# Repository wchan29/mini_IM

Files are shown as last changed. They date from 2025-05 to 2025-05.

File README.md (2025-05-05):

# mini_IM 
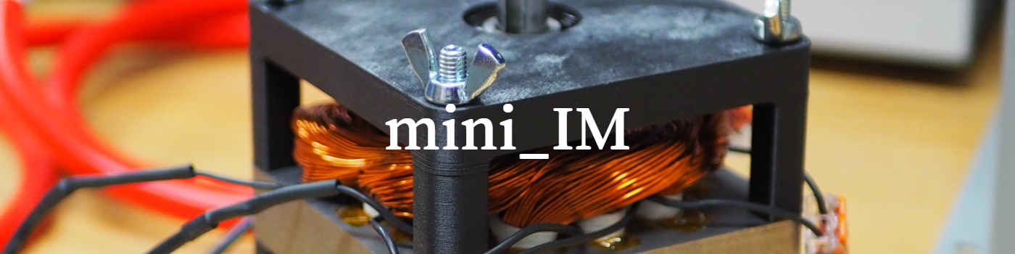
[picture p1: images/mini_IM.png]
mini_IM_banner


[][cc-by-nc]




## About
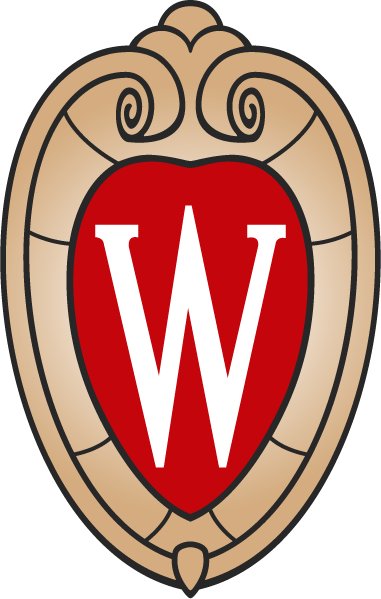
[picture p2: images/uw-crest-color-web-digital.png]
> 
> Compact Induction Machine with 3D Printed Housing. 
> 2021 UW-Madison Senior Design Project.

This project involves the design and prototyping of a compact, low-voltage induction machine kit for future use in UW-Madison's electrical engineering courses. Commissioned by the Grainger Teaching Studio, the kit supports a new hands-on power conversion class. This repository documents iterations developed by the senior design team.

**Team Memeber:** Anson Chan , Jon Keller, Steven Gerbers, Nathan Seibold <br>
**Post**: [Blog Post](https://wchan29.github.io/portfolio/wempec_induction_3d/)

### Rendering
<div style="display: flex; gap: 10px; align-items: flex-start;">
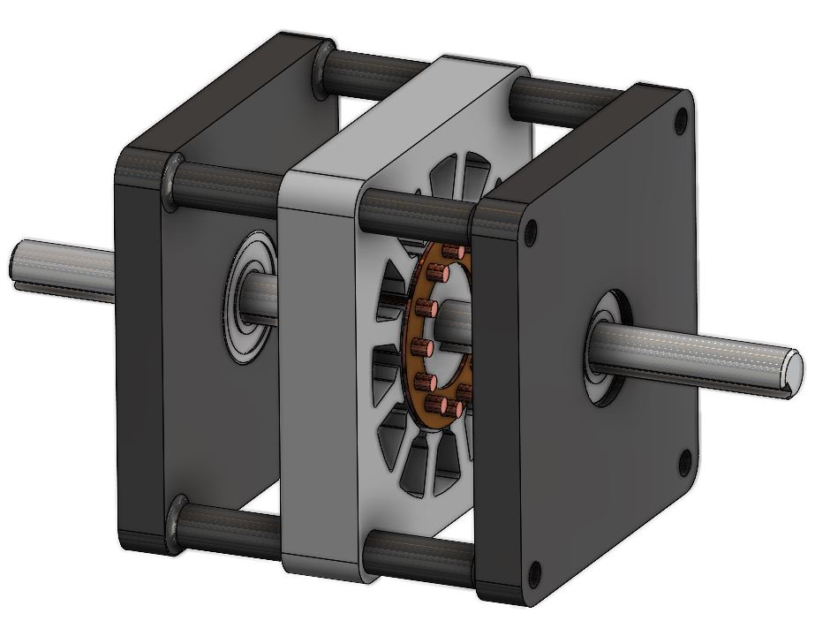
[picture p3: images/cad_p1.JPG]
  
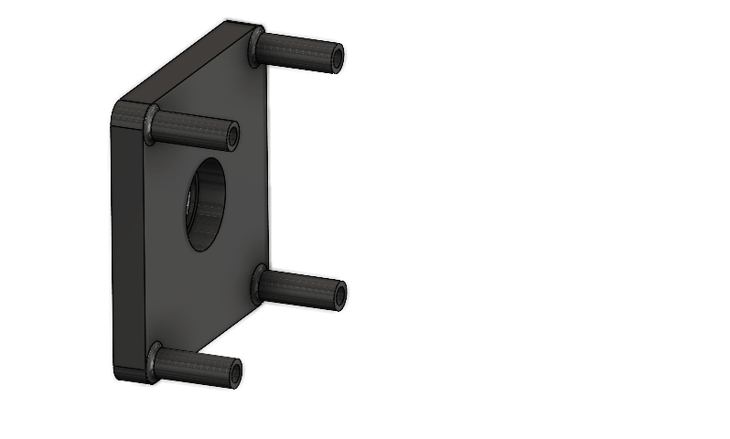
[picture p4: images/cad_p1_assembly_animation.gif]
  
</div>

## License
[][cc-by-nc]

This work is licensed under a
[Creative Commons Attribution-NonCommercial 4.0 International License][cc-by-nc].

[][cc-by-nc]

[cc-by-nc]: https://creativecommons.org/licenses/by-nc/4.0/
[cc-by-nc-image]: https://licensebuttons.net/l/by-nc/4.0/88x31.png
[cc-by-nc-shield]: https://img.shields.io/badge/License-CC%20BY--NC%204.0-lightgrey.svg

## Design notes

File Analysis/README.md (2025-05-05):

# Analysis 
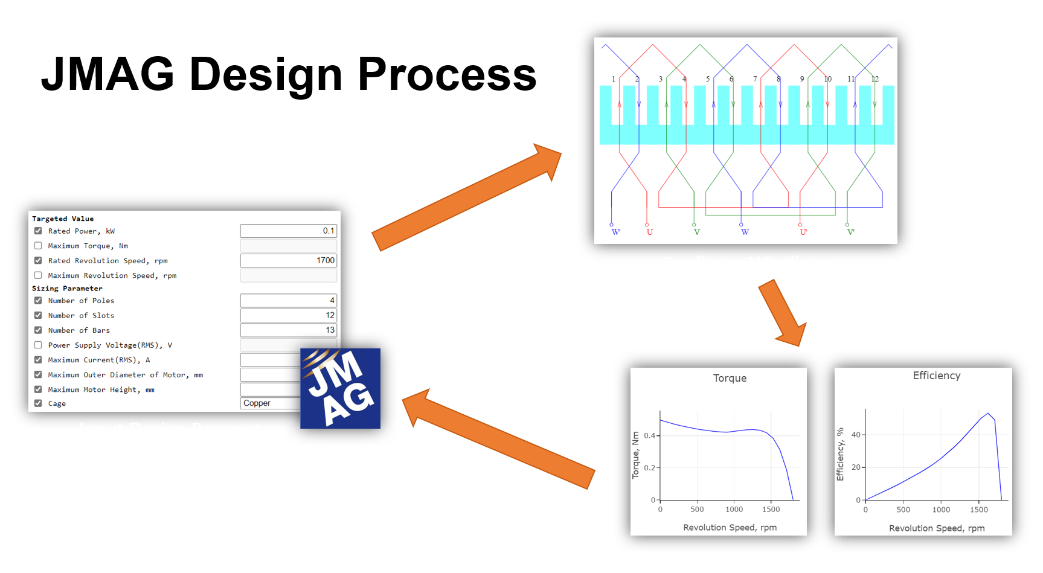
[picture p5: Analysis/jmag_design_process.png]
mag_design_process


## Related Documents
- [pd.jmd](./p3.jmd) - JMAG Express project file for p3 prototype

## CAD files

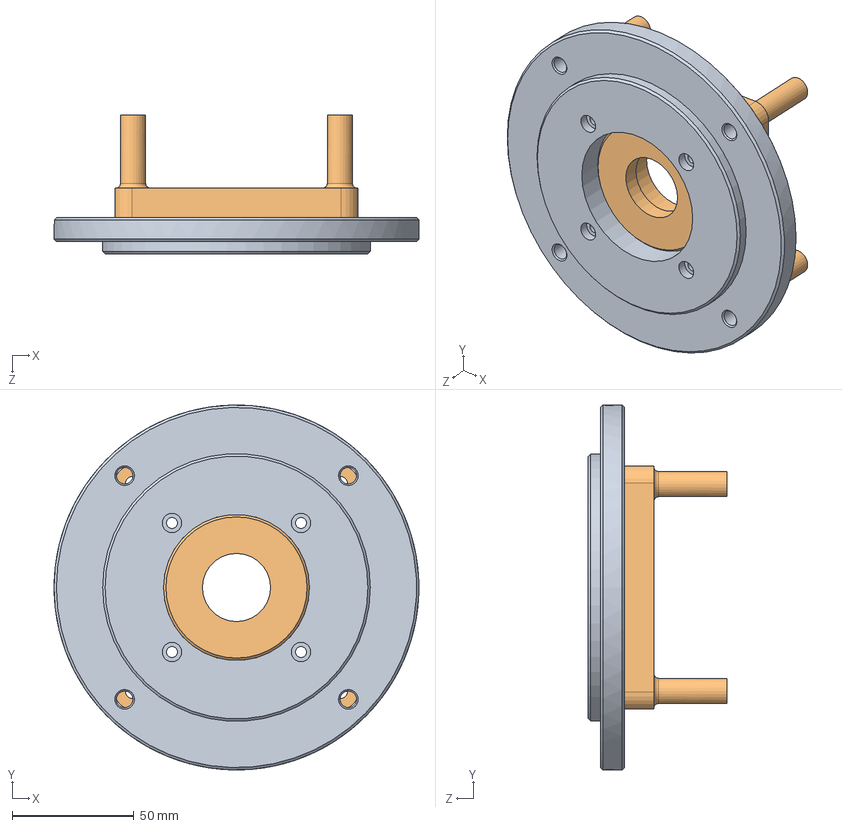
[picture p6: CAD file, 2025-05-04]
CAD/adapter_plate/Assem1.SLDASM
150.0 x 149.9 x 57.0 mm
adapter_plate
housing_plate

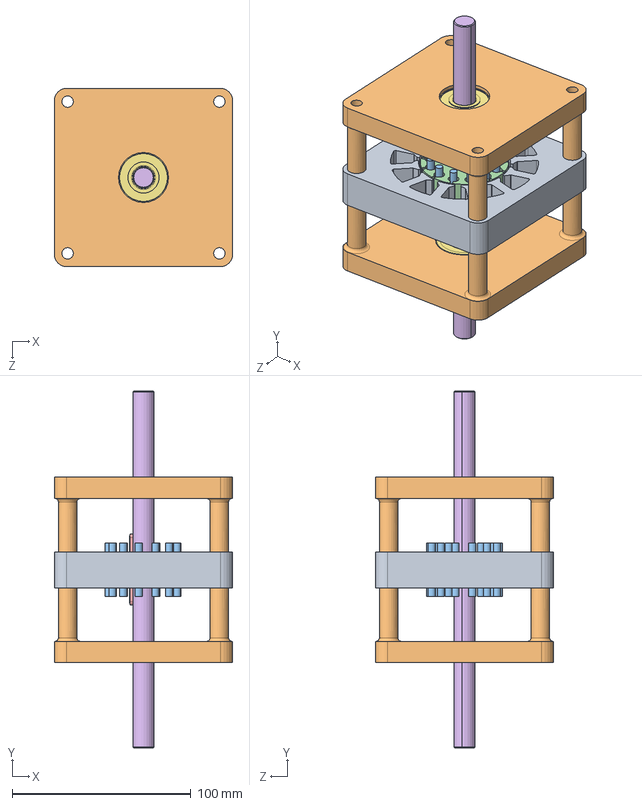
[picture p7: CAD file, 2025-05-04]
CAD/prototype_2/!p2_PrototypeAssmebly.SLDASM
100.0 x 200.0 x 100.0 mm
p2_stator_lamination
p2_housing_plate x 2
p2_copper_bars x 13
p2_rotor_lamenation
p2_shaft_key_KES4_40
p2_shaft_SFHKR12_200_KA80_A40
p2_Ball_Bearing_B6201ZZNR x 2

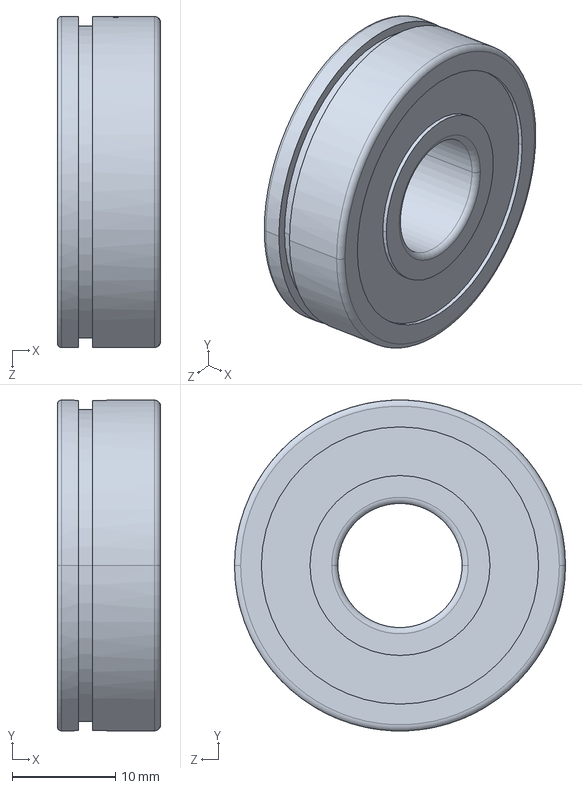
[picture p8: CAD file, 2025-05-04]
CAD/prototype_3/B6201ZZNR.sldasm
10.0 x 32.0 x 32.0 mm

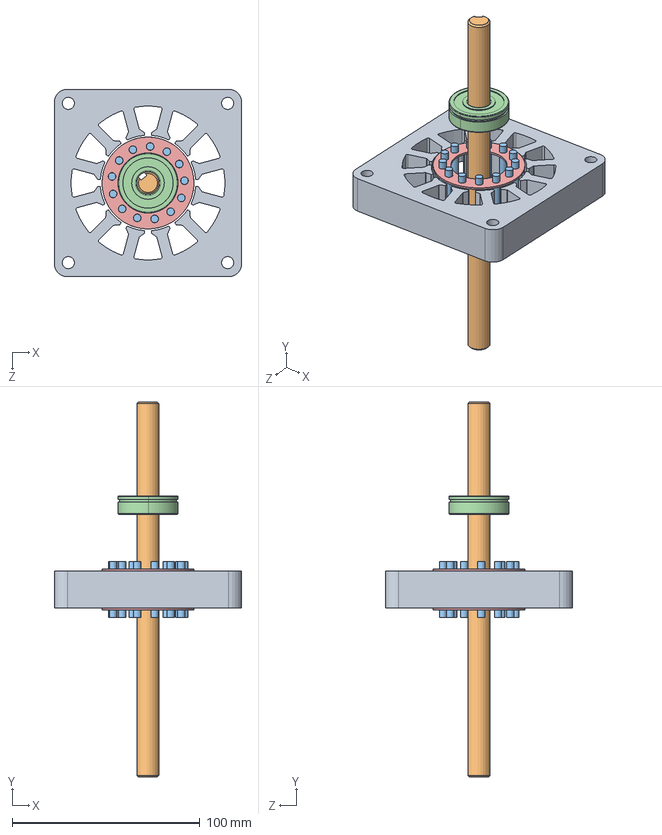
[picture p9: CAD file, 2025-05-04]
CAD/prototype_1/!p1_PrototypeAssmebly.SLDASM
100.0 x 200.0 x 100.0 mm
7398K215_304 STAINLESS STEEL KEYED ROTARY SHAFT
p1_copper_bars x 13
p1_copper_endplate x 2

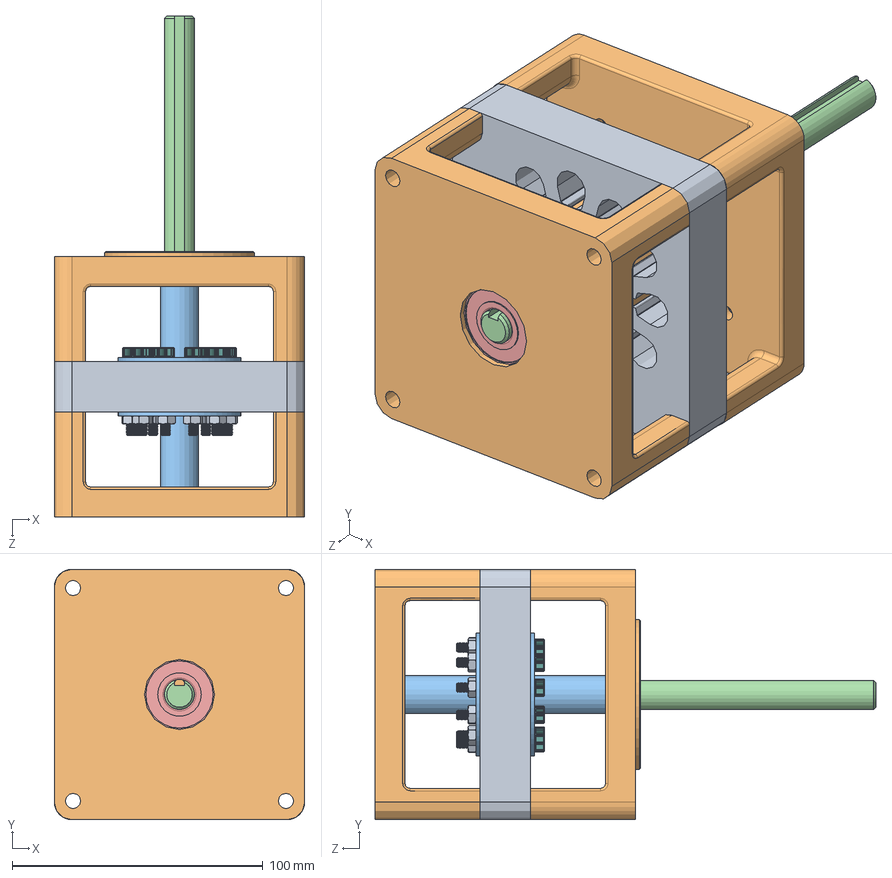
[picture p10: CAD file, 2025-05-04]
CAD/prototype_3/p3_assembly.SLDASM
100.0 x 100.0 x 200.0 mm
p3_stator
p3_rotor_hex_standoff
p3_aluminum_endplate x 2
7398K215_304 STAINLESS STEEL KEYED ROTARY SHAFT
_bearingB6201ZZNR_2 x 2
94180A353_Tapered Heat-Set Inserts for Plastic x 4
p3_aluminum_standoff_20mm_8mm x 11
M4 x 11
M4_Nut x 11
housing_plate_hex x 2
p3_rotor_spacer x 2

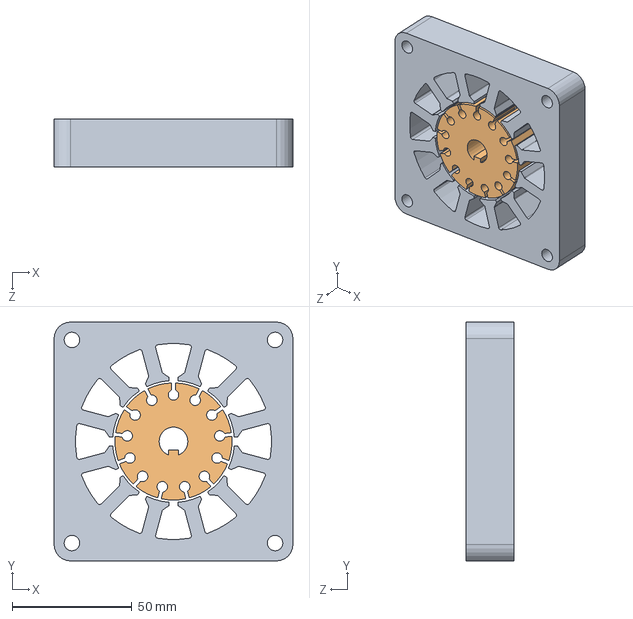
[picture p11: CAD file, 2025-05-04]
CAD/prototype_1/p1_lamination_assembly.SLDASM
100.0 x 100.0 x 20.0 mm
p1_stator_lamination
p1_rotor_lamenation

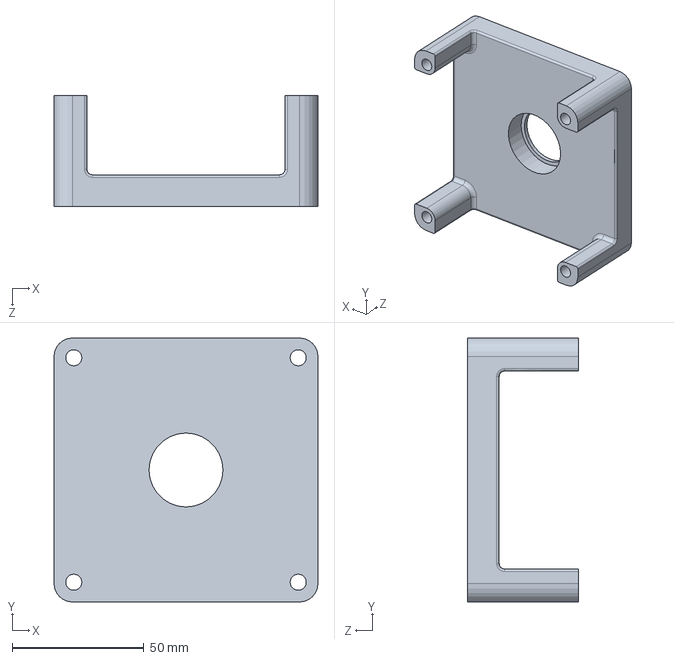
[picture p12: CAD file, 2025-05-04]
CAD/adapter_plate/housing_plate.SLDPRT
100.0 x 100.0 x 42.0 mm

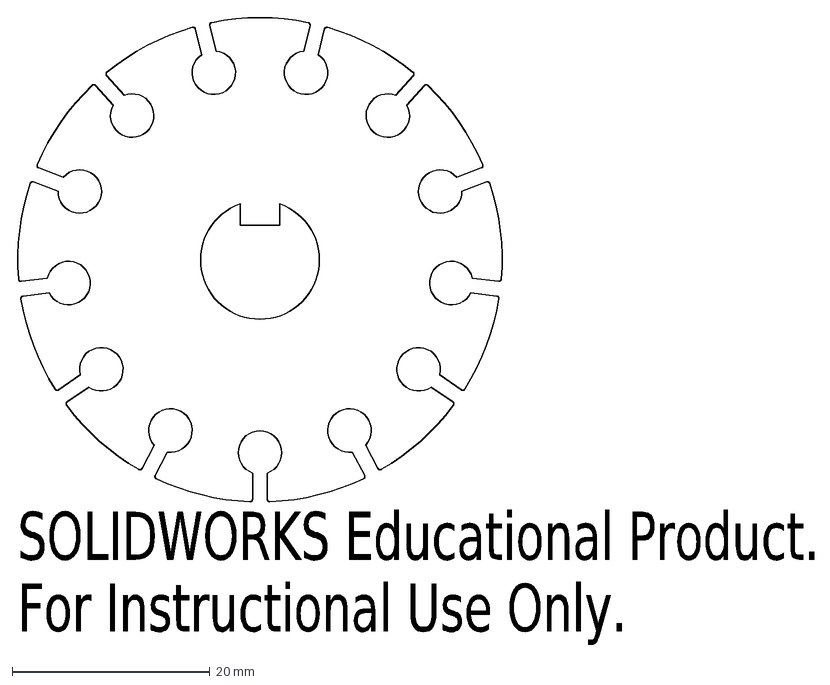
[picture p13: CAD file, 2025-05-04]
CAD/prototype_1/LaserCutting/p1_rotor_lamenation_v2.DXF
SOLIDWORKS Educational Product.
For Instructional Use Only.

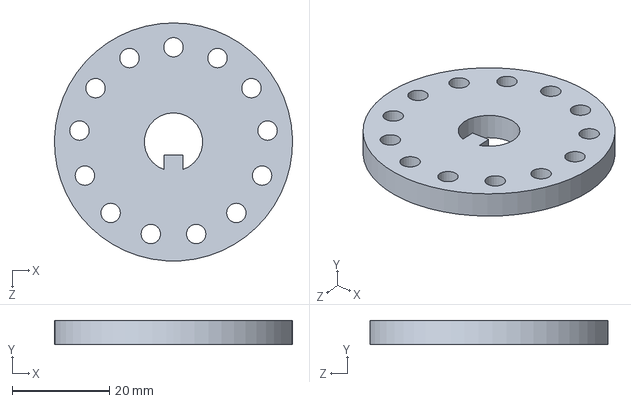
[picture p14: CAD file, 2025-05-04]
CAD/prototype_1/p1_endplates.SLDPRT
49.0 x 5.00 x 49.0 mm

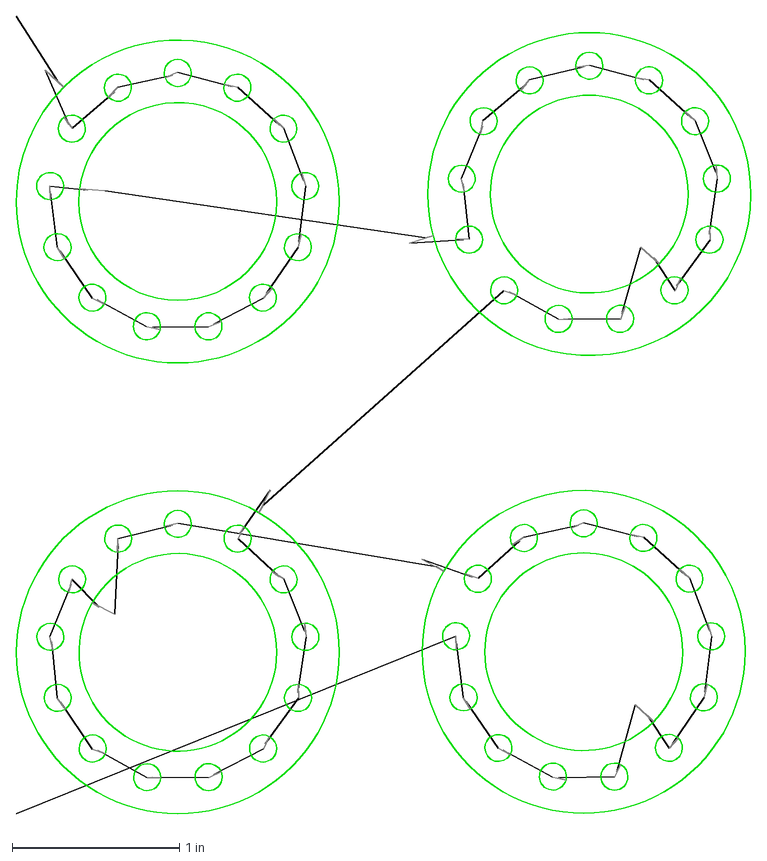
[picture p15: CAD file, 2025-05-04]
CAD/prototype_1/Waterjet/p1_copper_endplate_imported_DXF.dxf
4.39 x 4.81 in

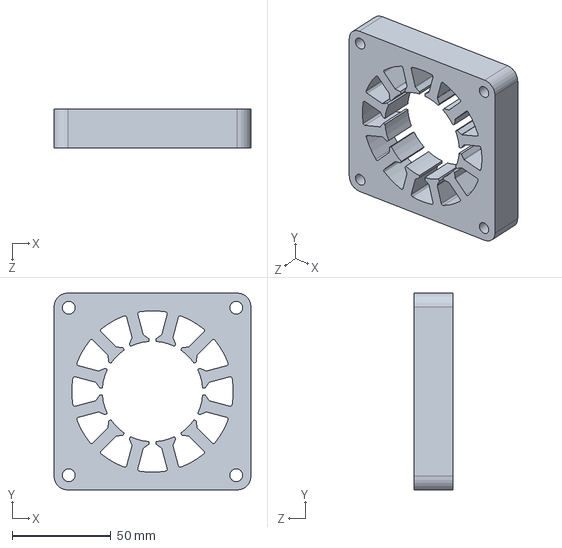
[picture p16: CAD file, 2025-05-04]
CAD/prototype_2/p2_stator_lamination.SLDPRT
100.0 x 100.0 x 20.0 mm

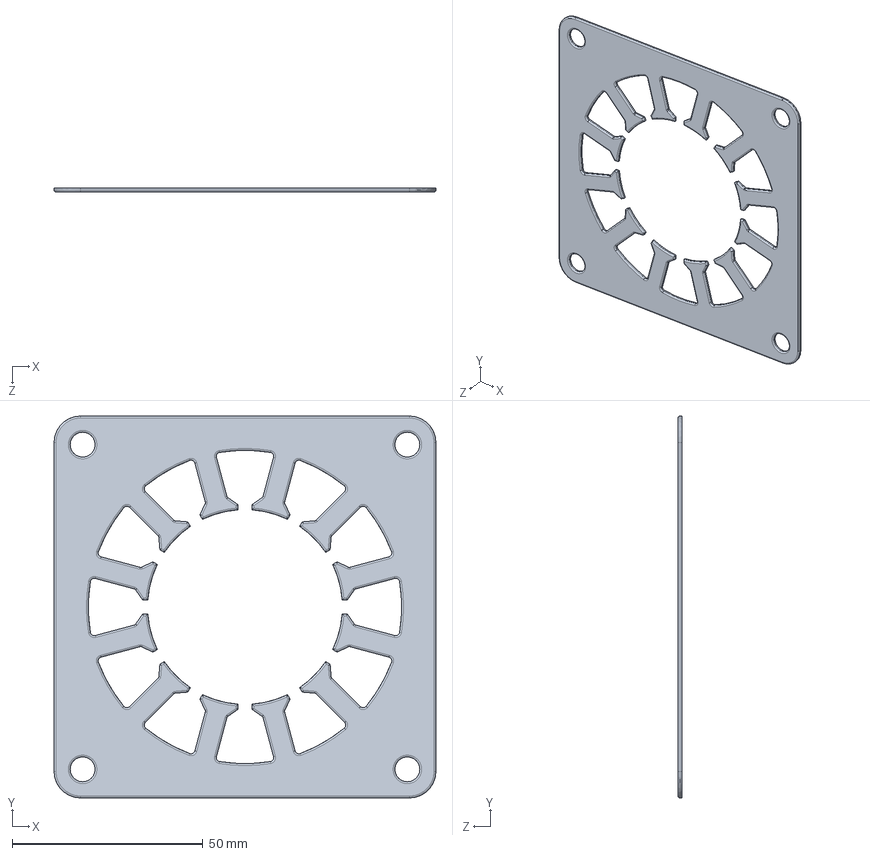
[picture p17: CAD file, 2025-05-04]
CAD/prototype_2/Winding Fixture/stator_lam_spacer.SLDPRT
100.0 x 100.0 x 1.00 mm

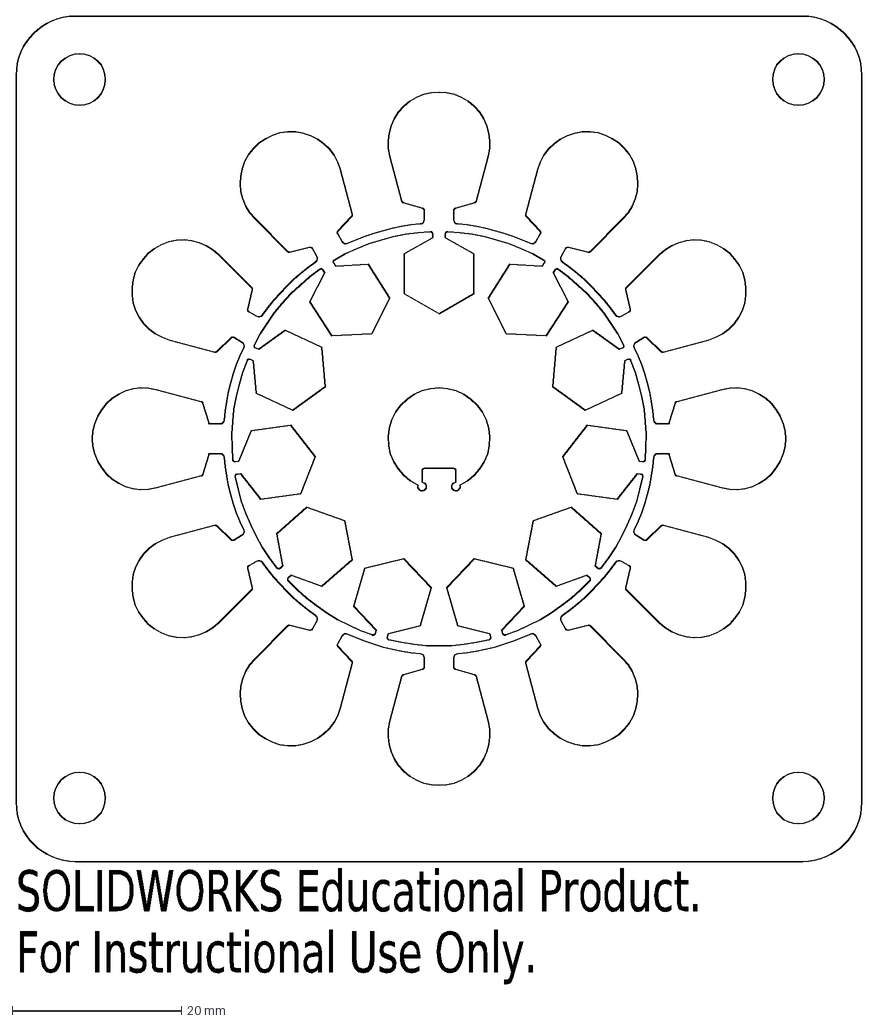
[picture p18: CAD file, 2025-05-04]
CAD/prototype_3/DXF/lamination_dxf.DXF
SOLIDWORKS Educational Product.
For Instructional Use Only.

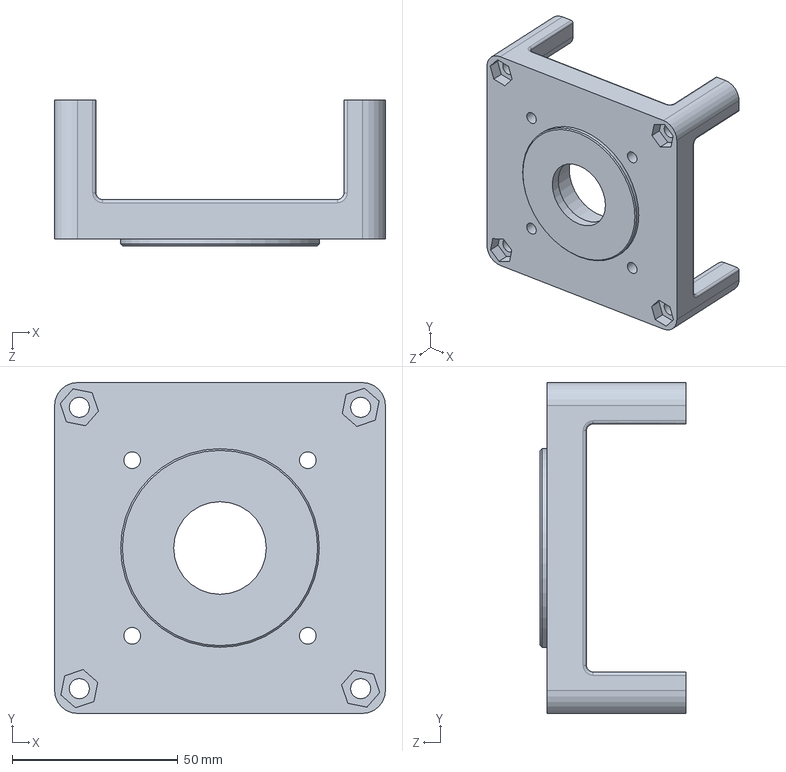
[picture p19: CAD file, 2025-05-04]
CAD/prototype_3/housing_plate.SLDPRT
100.0 x 100.0 x 44.0 mm

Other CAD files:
CAD/prototype_1/B6201ZZNR.sldasm
CAD/prototype_3/Slot Endplate/Slot_Endplate.SLDPRT
CAD/prototype_3/Slot Spacer/winding_slot_spacer.SLDPRT
CAD/prototype_3/STL/housing_plate_hex.SLDPRT
CAD/adapter_plate/94180A353_Tapered Heat-Set Inserts for Plastic.SLDPRT
CAD/adapter_plate/adapter_plate.SLDDRW
CAD/adapter_plate/adapter_plate.SLDPRT
CAD/prototype_1/7398K215_304 STAINLESS STEEL KEYED ROTARY SHAFT.SLDPRT
CAD/prototype_1/Assem1.SLDPRT
CAD/prototype_1/LaserCutting/copperends_forpia.DXF
CAD/prototype_1/LaserCutting/p1.DXF
CAD/prototype_1/Waterjet/p1_copper_endplate.DXF
CAD/prototype_1/_bearingB6201ZZNR_2.sldprt
CAD/prototype_1/p1_copper_bars.SLDPRT
CAD/prototype_1/p1_copper_endplate.SLDPRT
CAD/prototype_1/p1_housing_plate.SLDPRT
CAD/prototype_1/p1_lamination_assembly.SLDDRW
CAD/prototype_1/p1_rotor_lamenation.SLDPRT
CAD/prototype_1/p1_stator_lamination.SLDPRT
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

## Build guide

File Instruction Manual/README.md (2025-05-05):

# Instruction Manual

## Related Documents
- [IM Drawings.pdf](/Instruction%20Manual/IM%20Drawings.pdf) - Induction machine (p3) engineering drawings. 
- [IM Instruction Manual.pdf](/Instruction%20Manual/IM%20Instruction%20Manual.pdf) - Induction machine assembly instruction manual. 

## Bill of Materials (BOM)

### **In House Parts**
| Item                  | Description                                                    | Material     | Source           | Quantity | Specifications           | Unit Price | Total Price |
| --------------------- | -------------------------------------------------------------- | ------------ | ---------------- | -------- | ------------------------ | ---------- | ----------- |
| Motor Housing         | 2 Unique Motor Housing End Plates                              | Onyx Polymer | Stocked in House | 1        | 100mm W x 100mm L        | $25.00     | $25.00      |
| Lamination Sheet      | Stator and rotor core laminations cut from stocked sheet metal | Steel        | Stocked in House | varies   | 0.025" th x ~300 sq. in. | $5.00      | $5.00       |
| Windings              | 21 gauge insulated copper wire                                 | Copper       | Stocked in House | 1        | N/A                      | $10.00     | $10.00      |
| Rotor Fasteners       | M4 bolts and lock nuts for rotor                               | Steel        | Stocked in House | 11       | M4 thread x 16mm L       | $5.00      | $5.00       |
| Electrical Connectors | Terminals and insulated banana plugs                           | N/A          | Stocked in House | 6        | N/A                      | $0.00      | $0.00       |
| Threaded Inserts      | M4 thermal set inserts                                         | Steel        | Stocked in House | 4        | M4                       | $0.00      | $0.00       |
| Loctite               | Applied to rotor standoff fasteners                            | N/A          | Stocked in House | N/A      | N/A                      | $0.00      | $0.00       |
| Stator Slot Retainers | Small 3D-printed tabs to constrain stator coils                | Onyx Polymer | Stocked in House | 12       | N/A                      | $0.00      | $0.00       |
|                       | **Subtotal:**                                                  |              |                  |          |                          |            | **$45.00**  |

### **Purchased Parts** 
| Item                     | Description                                               | Material      | Source                               | Quantity | Specifications                      | Unit Price | Total Price |
| ------------------------ | --------------------------------------------------------- | ------------- | ------------------------------------ | -------- | ----------------------------------- | ---------- | ----------- |
| Bearings                 | 6201 open ball bearings                                   | Steel         | McMaster-Carr [5972K313]             | 2        | 12mm ID                             | $6.06      | $12.12      |
| Shaft                    | Rotary shaft with full-length keyway                      | Steel         | McMaster-Carr [7398K215]             | 1        | 200mm L x 12mm OD                   | $13.93     | $13.93      |
| Housing Fasteners        | Fasteners to secure the housing plates                    | Steel         | Fastenal [Bolts:11113709 Nuts:90673] | 4        | Bolts: M6-1 x 130mm L<br>Nuts: M6-1 | $2.40      | $9.60       |
| Rotor End Plates         | Aluminum ring-shaped rotor end plates cut from flat stock | 6061 Aluminum | McMaster-Carr [89015K184]            | 0.125    | 0.063" th x 6" W x 12" L            | $11.53     | $1.44       |
| Aluminum Rotor Standoffs | Male female M4 threaded hex standoff for rotor cage       | 6061 Aluminum | McMaster-Carr [98952A155]            | 11       | 8mm hex x 20mm L                    | $1.62      | $17.82      |
|                          | **Subtotal:**                                             |               |                                      |          |                                     |            | **$54.91**  |
|                          | **Total:**                                                |               |                                      |          |                                     |            | **$99.91**  |

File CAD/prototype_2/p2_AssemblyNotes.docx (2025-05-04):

Used 24 gauge wire

165 turns with 2 bundle fill (40%)

Unacceptable won’t fit in stator slot

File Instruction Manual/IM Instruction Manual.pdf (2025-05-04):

1 | P a g e

# Induction Machine Fabrication Manual

### Spring and Fall 2021

Nathaniel Seibold

Jonathan Keller

Anson Chan

Steven Gerbers

### Table of Contents

## 1 Introduction

### 1.1 Purpose

The purpose of this manual is to provide a step-by-step assembly process for a low-voltage induction machine built at the WEMPEC Lab at University of Wisconsin-Madison. This manual includes detailed descriptions and visual aids portraying the fabrication of parts at various stages of the build and the assembly of the motor based on a standard design.

The machine that will be assembled was designed with an emphasis on manufacturability. The motor covered in this manual is a basic 3-phase, 4-pole, 12 slot, single-layer winding, squirrel-cage rotor induction machine. The manual will cover basic working principles of an induction machine followed by the sequential steps to build one. The subassemblies include the rotor, stator and end plates. The rotor and stator assemblies will lead into the testing section, which will walk the user through the process of setting up and performing the High-Pot test. The end plates and final assembly will be put together at the conclusion of the High-Pot test.

Figure 1. Fully assembled 4-pole, 12 slots, squirrel-cage rotor induction motor.

### 1.2 Technical Background

Induction machines, also known as asynchronous machines, are one of the most widely used electrical motors in both domestic and industrial applications. In fact, about 50 percent of global power is consumed by electric machines and over 90 percent of industrial machines are induction motors. The high efficiency combined with low maintenance and self-starting properties makes the induction machine one of the most popular choices within the industry.

An induction machine comprises of two main components, the stationary stator, and a rotating rotor. An exploded view of a common industrial squirrel cage type induction machine is shown in Figure 2. The main frame, typically made from cast iron, is used to house and protect the stator and rotor from damage as well as protect the user while operating. While sometimes not necessary, fans are also added to the machine to prevent the stator coils from overheating.

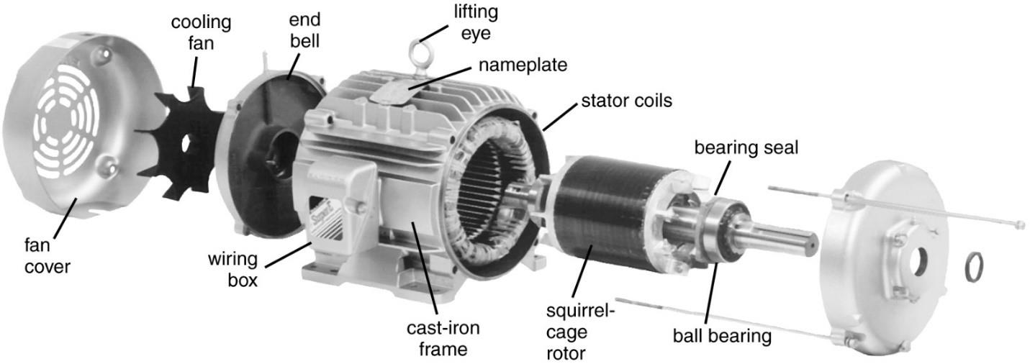
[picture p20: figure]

Figure 2. An exploded view of a squirrel-cage type induction motor.

A cross-sectional view of an induction machine is shown in Figure 3. The stator is composed of stator windings and iron laminations. The copper windings in the stator are typically wounded in a distributed fashion, meaning they are typically spread throughout the stator lamination. Since an induction machine typically has three phases, the windings would have three individual input terminals. When the windings in the stator are connected to a three-phase power source, a rotating magnetic field is generated. Note that this is a fundamentally different supply than that from a wall outlet, so this motor will have to be operated in the lab with the correct power supply.

Figure 3. Cross-sectional view of a squirrel cage type induction machine stator and rotor.

One of the most common rotor designs for induction machine is the squirrel cage design. The construction of the squirrel cage rotor is shown in Figure 4 below.

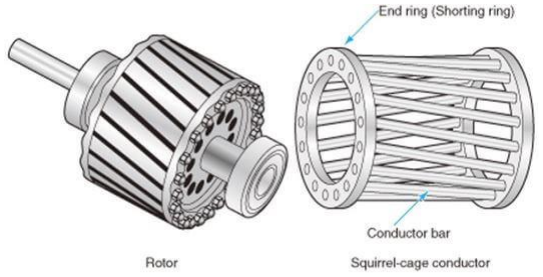
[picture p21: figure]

Figure 4. Construction of a squirrel-cage rotor.

The squirrel cage rotor design uses conducting bars (typically made from copper and/or aluminum) connected to an end ring on either end. Within the cage, iron laminations are added to assist the flow of magnetic flux generated by the stator windings. A current is induced in the rotor bars when a rotating magnetic field is generated by the stator windings. The interactions between the induced current in the rotor and the rotating magnetic field in the stator allows the generation of torque in the squirrel cage rotor, creating a rotating motion. As seen above, the bars are skewed at an angle. This is to prevent cogging, which is a locking of the rotor upon startup that commonly occurs when using an equal number of conductor bars and stator teeth.

## 2 Parts List and Description

Many parts needed for this induction motor are stocked in-house, including copper wire and steel laminations. However, parts such as the rotary shaft and bearings must be purchased from external vendors. All the parts used in this design are shown in Table 1.

Table 1. Full Assembly Bill of Materials.

Bill of Materials

Item | Description | Material | Source | Quantity | Specifications | Unit Price | Total
| | | | | | | Price
In House Parts
Motor Housing | 2 Unique Motor
| Housing End Plates | Onyx
| | Polymer | Stocked in House | 1 | 100mm W x
| | | | | 100mm L | $25.00 | $25.00
Lamination Sheet | Stator and rotor core
| laminations cut from
| stocked sheet metal | Steel | Stocked in House | varies by
| | | | sheet
| | | | size | 0.025" th x
| | | | | ~300 sq. in. | $5.00 | $5.00
Windings | 21 gauge insulated
| copper wire | Copper | Stocked In House | 1 | N/A | $10.00 | $10.00
Rotor Fasteners | M4 bolts and lock nuts
| for rotor | Steel | Stocked In House | 11 | M4 thread x
| | | | | 16mm L | $5.00 | $5.00
Electrical Connectors | Terminals and insulated
| banana plugs | N/A | Stocked In House | 6 | N/A | $0.00 | $0.00

Threaded
Inserts | M4 thermal set inserts | Steel | Stocked in House | 4 | M4 | $0.00 | $0.00
Loctite | Applied to rotor
| standoff fasteners | N/A | Stocked In House | N/A | N/A | $0.00 | $0.00
Stator Slot Retainers | Small 3D-printed tabs to
| constrain stator coils | Onyx
| | Polymer | Stocked In House | 12 | N/A | $0.00 | $0.00
| | | | | | Subtotal: | $45.00

Purchased Parts
Bearings | 6201 open ball bearings | Steel | McMaster-Carr
| | | [5972K313] | 2 | 12mm ID | $6.06 | $12.12
Shaft | Rotary shaft with full-
| length keyway | Steel | McMaster-Carr
| | | [7398K215] | 1 | 200mm L x
| | | | | 12mm OD | $13.93 | $13.93
Housing Fasteners | Fasteners to secure the
| housing plates | Steel | Fastenal
| | | Bolts:[11113709]
| | | Nuts:[90673] | 4 | Bolts: M6-1 x
| | | | | 130mm L
| | | | | Nuts: M6-1 | $2.40 | $9.60

Rotor End
Plates

Aluminum ring-shaped
rotor end plates cut
from flat stock

6061
Aluminum

McMaster-Carr

[89015K184] | 0.125 | 0.063" th x 6"
W x 12" L | $11.53 | $1.44

Aluminum
Rotor
Standoffs

Male female M4
threaded hex standoff
for rotor cage

6061
Aluminum

McMaster-Carr

[98952A155] | 11 | 8mm hex x
20mm L | $1.62 | $17.82
Subtotal: | $54.91
Total: | $99.91
Note: In house material prices are an estimate only. Purchased part prices and supply may fluctuate.

For the motor that this manual is based around, one would expect to spend approximately $50 on purchased parts. An estimate of $40-50 of in-house part cost to the lab brings the total cost estimate to the desired limit of $100 per motor. As this design focuses on a single motor having extremely high manufacturability, there is plenty of room for cost minimization in alternative designs and high-volume orders.

Certain considerations were implemented in the effort of saving raw material, money, and time. The aluminum flat sheet stock used for the rotor end plates was oversized and thus each build only requires a portion of the sheet. The rotor laminations are superimposed concentrically with the stator laminations, dramatically reducing the amount of waste. The rotary shaft with a full-length keyway was chosen with respect to simplicity and price by eliminating the need for a standard machine key, which was used in one of the iterative motor designs. The rotor assembly can be very flexible in terms of design constraints, and several unique designs were tested before deciding on the final design. Possible rotor design changes are discussed further in the Rotor section.

## 3 Assembly

The induction machine has three main assemblies, each of which will be built independently and assembled once all are completed. The subassemblies include the rotor, stator, and end plates. The end plates are 3D printed and require minimal further assembly. The rotor and stator represent the working principles of the machine and are the most intensive components to manufacture. The fabrication of rotor and stator parts requires the use of a laser cutter, winding jig, soldering iron, and other miscellaneous tools, all of which can be found in the WEMPEC lab.

### 3.1 Rotor

The rotor spins due to its interaction with the rotating magnetic field generated by the stator windings, and it is what produces mechanical work from the input of the electrical work. The rotor is commonly from materials such as solid copper bars or cast aluminum with shorted end-rings for electrical conduction.

Instead of implementing the skewed rotor cage design, the rotor that will be covered in this section is a non-skewed cage design was implemented to simplify the manufacturing process. Additionally, threaded aluminum standoffs are used in place of solid copper for the conducting bars. This is because a copper rotor requires the process of soldering, and aluminum standoffs can simply be fastened with nuts and bolts, drastically increasing manufacturability.

Figure 5. Final rotor assembly.

Parts and Materials

The parts and their respective quantities are shown in Table 2 along with a picture in Figure 5. The rotor mainly consists of the keyed rotary shaft and the core, which consists of stacked laminations and the squirrel cage components. In this design, aluminum standoffs fastened to an aluminum end ring (creating the squirrel-cage) were used to create the shorted circuit for the induced current. The rotor cage can be made from aluminum or copper, but their difference in conductivity requires a correction to the cross-sectional area of conductor needed. Generally, the conductivity of aluminum is about 60 percent of the conductivity of copper.

The rotor laminations are the smaller of the two laminations cut together from steel sheet metal stocked in the lab. The rotor lamination stack should be equal in height to the stator lamination stack. The tabs present in the center hole of the rotor laminations stack to create an integrated key that should fit snug on the keyed rotary shaft. The final rotor assembly can be found in Figure 6.

Table 2. Parts needed for rotor assembly.

Part | Quantity
Keyed Rotary Shaft (not pictured) | 1
Steel Rotor Laminations | ~31
8mm x 20mm Aluminum Standoff | 11
Aluminum End Plate | 2
M4 Lock Nuts | 11
M4 Fasteners | 11
Locktite | 1

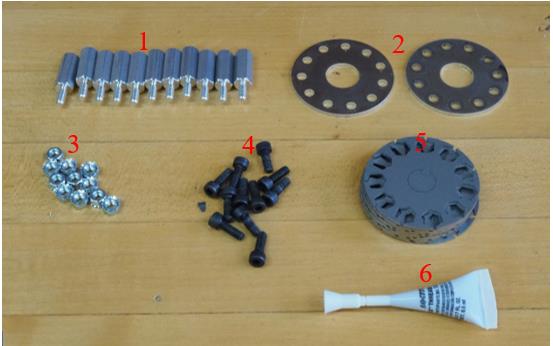
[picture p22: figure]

Figure 6. Parts needed for rotor assembly.

3.1.1 Place rotor laminations onto rotor shaft
Prepare the rotor laminations by removing all excess material left from the laser-cutting process, making sure not to bend the slot tabs. Slide each lamination onto the rotary shaft, ensuring that all are stacked in the same orientation. Figure 8 shows an improper mix of lamination orientations.

Figure 7 (Left): Placing rotor laminations on the rotary shaft.

Figure 8 (Right): Lamination when not stacked in the same orientation. Visible through the shininess on the side
3.1.2 Measure rotor lamination stack length
Use calipers to measure the final thickness of the rotor laminations. Each lamination is 0.025 [in] thick, and the final thickness should be at or just under 0.787 [in], or 20 [mm]. This translates to an estimated 31 laminations needed. A thickness of over 20 [mm] would prevent the alumnium endplate from having full contact with the standoffs.

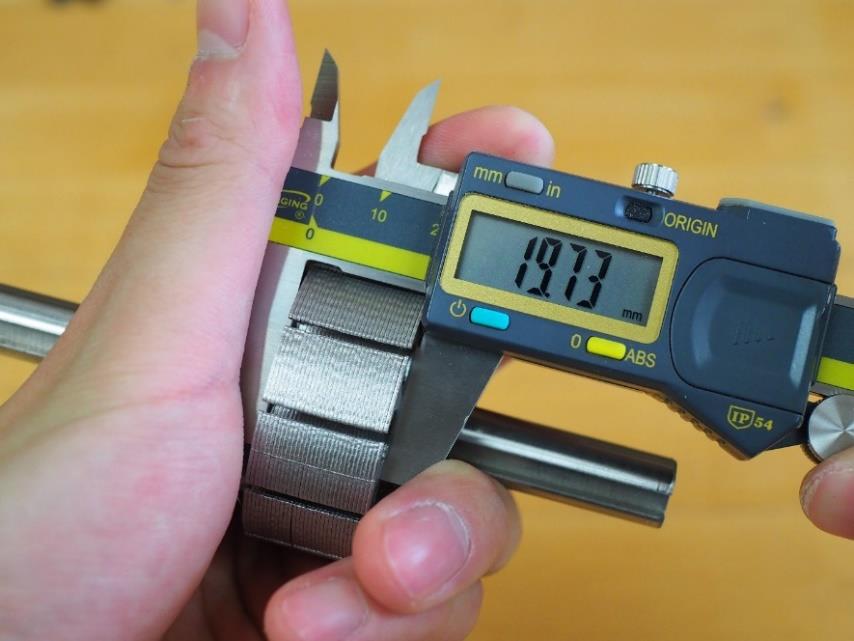
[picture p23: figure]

Figure 9. Ensure the rotor lamination thickness is at or no greater than 20 [mm].

3.1.3 Place the standoffs in the rotor slots
Align the rotor laminations and place the standoffs into the hexagonal slots. Some force may be required depending on the accuracy of the stack alignment. The female end should be flush with the top of the rotor core, and all standoffs should face the same direction.

Figure 10. Placing the standoffs through the rotor laminations.

3.1.4 Sand and install the first end plate
The rotor end plates are cut from a 0.063 [in] thick multipurpose 6061 aluminum sheet. Clean the endplate surface by using sand paper and place it on the threaded end. Sanding and cleaning the end plates are necessary to ensure low contact resistance between the ring and standoffs.

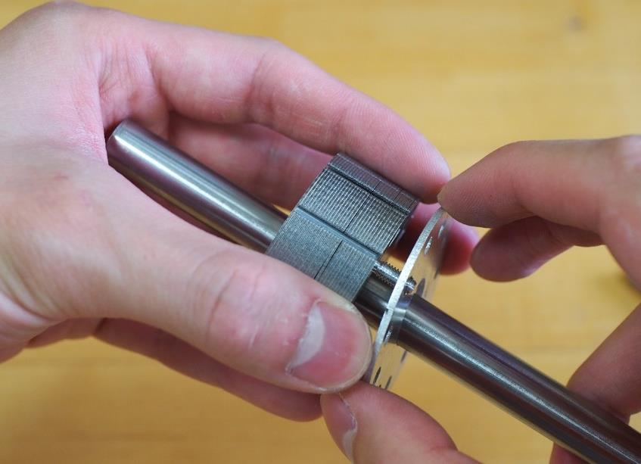
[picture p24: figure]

Figure 11. Placing one end plate through the male ends.

3.1.5 Set the locking nuts in place
Place a lock nut on the male end of the standoff and tighten it with hand. Repeat for all remaining slots. Visually ensure that all lock nuts sit flush on the end ring with the standoffs unable to shift in that direction.

Figure 12. Adding locking nuts to the male end of the standoffs.

3.1.6 Apply Locktite and screw on fasteners
Place the other aluminum endplate on the bottom of the rotor core. Apply a small amount of locktite (a one drop) on the M4 fasteners and tighten them by hand into the female end of the standoffs. Again, there should be no clearance between the fastener head and the end ring.

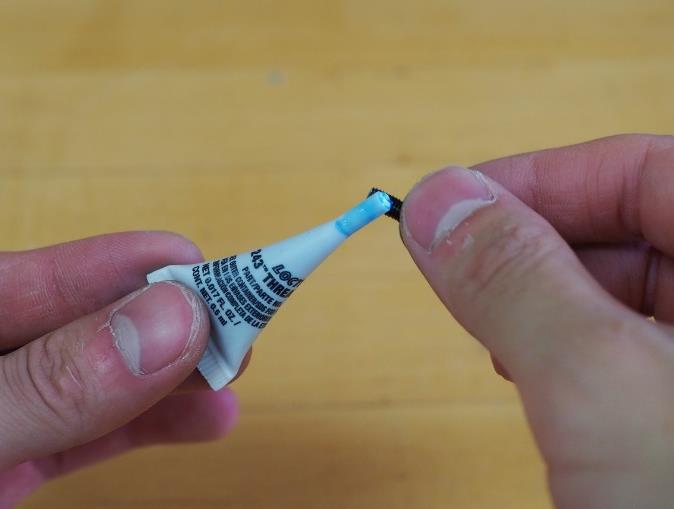
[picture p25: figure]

Figures 13 (Left) and 14 (Right). Applying the Loctite and placing the fasteners in the female end of the standoff.

3.1.7 Tighten the assembly
Tighten all the lock nuts using a needle pliers or wrench. Use an Allen wrench to tighten the M4 fasteners on the other end. Ensure a snug, even fit all around to conclude the rotor assembly process.

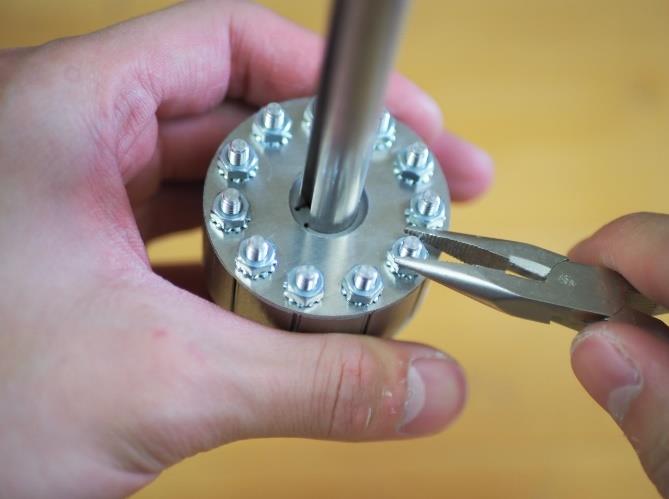
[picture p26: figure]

Figures 15 (Left) and 16 (Right). Tightening both sides of the aluminum standoffs.

### 3.2 Stator

The stator of the motor is comprised of two main components: steel laminations and copper windings. This is one of the most delicate and critical pieces of the motor assembly process, so it is critical that each step be followed precisely and carefully. The stator generates the rotating magnetic field and is the part of the motor with supplied excitation current/voltage.

This stator is designed with 12 slots and has single layer windings with a 40% fill-factor. While a double-layer wound machine has a better efficiency due to less harmonic fluxes, a single-layer wound machine is easier to manufacture due to its simplified winding configuration. The coils utilized in the stator must not be shorted together whatsoever, so the insulated coating must not be damaged. To help avoid accidental shorts, the stator slots will be lined. Each coil must be the same length to ensure that the resistance is the same for each phase.

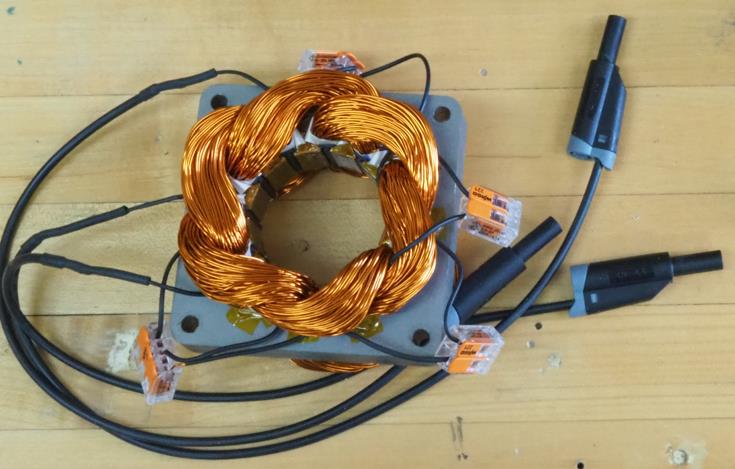
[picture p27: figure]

Figure 17. Final stator assembly.

Parts and Materials

Table 3. Parts needed for stator assembly.

Part | Quantity
Steel Stator Laminations | ~31
Polyimide Tape | N/A
21 AWG Copper Wire | N/A
Winding Jig | 1
3D Printed Stator Slot Retainers | 12
Folded Insulation Paper | 12
Clamp Down Wire Connectors (2 terminals) | 3
Clamp Down Wire Connectors (3 terminals) | 1
Banana Plugs | 3

3.2.1 Stack stator laminations
Stack all steel stator laminations together ensuring that each lamination is stacked in the same orientation just like the rotor laminations. The side with the better finish should point towards the top of the motor. The different sides can be seen and compared in Figure 3 above. Stacking them in the correct orientation, while not critical, can help with the reduction of eddy currents in the stator and general alignment of the assembly. Use M6 fasteners and wing nuts to secure the stator laminations together. 3D printed slot retaining tabs were implemented to help with the stator winding process and they should be printed before starting that process.

Once the lamination stack is completed, generously apply polyimide tape to the interior edges of the stator. Ensure the tape fully covers each slot, especially the edges, to help prevent shorts.

Figure 18 (Left) and 19 (Right). Polyimide tape applied to stator slots
3.2.2 Insert insulation paper into slots
Cut 12 pieces of insulation paper approximately 36mm x 31mm in size. Fold them as shown in Figure 21 below. Roll the paper strips with a round screwdriver to form the slot shape and insert one into each stator slot, as shown below in Figures 22, 23, and 24.

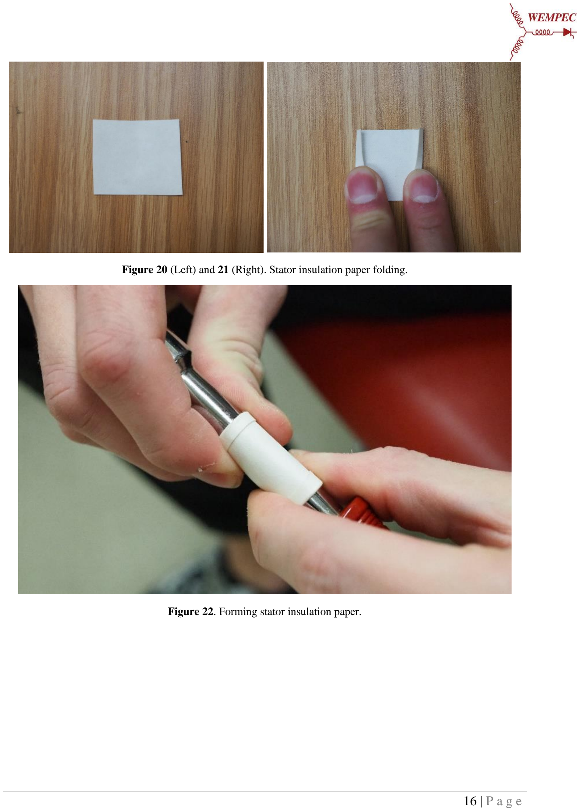
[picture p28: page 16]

Figure 20 (Left) and 21 (Right). Stator insulation paper folding.

Figure 22. Forming stator insulation paper.

Figure 23 (Left) and Figure 24 (Right). Polyimide tape applied to stator slots

3.2.3 Setting up the winder
To wind the copper windings, the Adams Maxwell Model 1400-3A or similar chuck-based winder should be used. An image of this winding machine is shown in the next figure.

Figure 25. Winding machine used for stator windings.

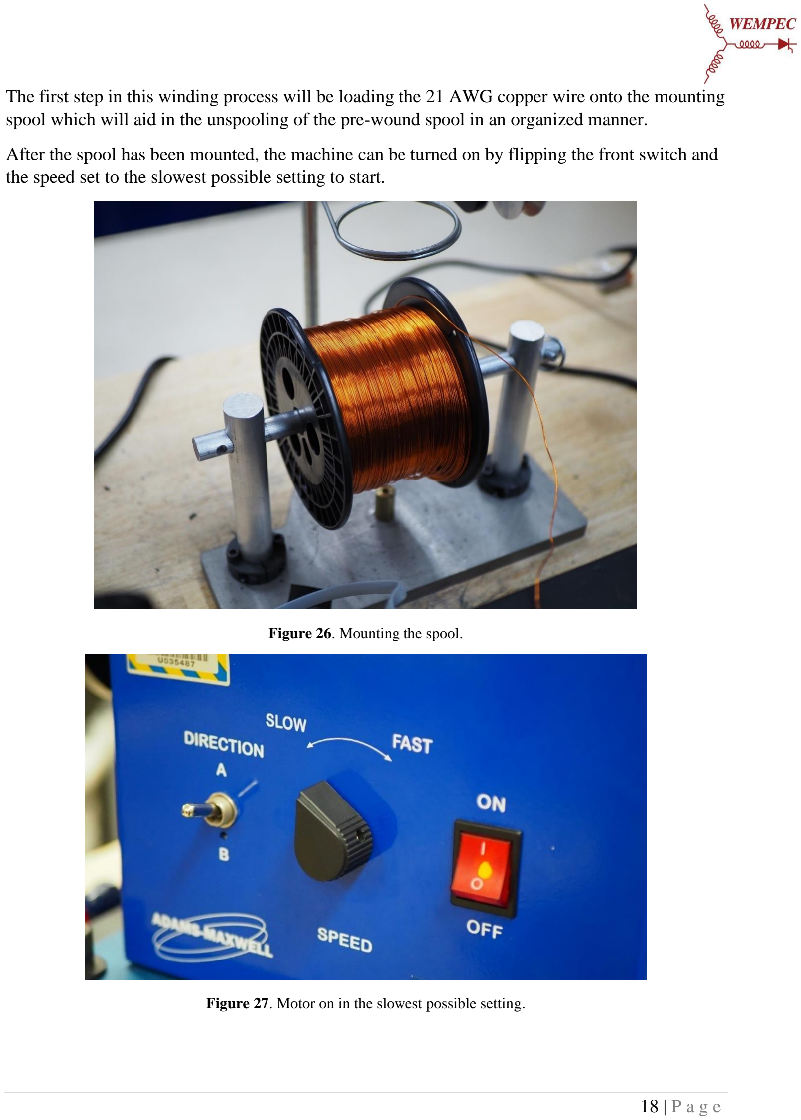
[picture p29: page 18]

The first step in this winding process will be loading the 21 AWG copper wire onto the mounting spool which will aid in the unspooling of the pre-wound spool in an organized manner.

After the spool has been mounted, the machine can be turned on by flipping the front switch and the speed set to the slowest possible setting to start.

Figure 26. Mounting the spool.

Figure 27. Motor on in the slowest possible setting.

3.2.4 Insert the winding jig
Insert the winding jig into the chuck and tighten hand tight by twising the largest diameter section while preventing the rest of the chuck from spinning.

Figure 28. Winding jig inserted into shuck

The dead center on the right should be moved into the piece. The dead center should be tight enough against the jig to prevent wobble but not tight enough to prevent the chuck from spinning. This can be done by loosening the 9/16” nut at the base of the dead center and sliding the dead center into the jig.

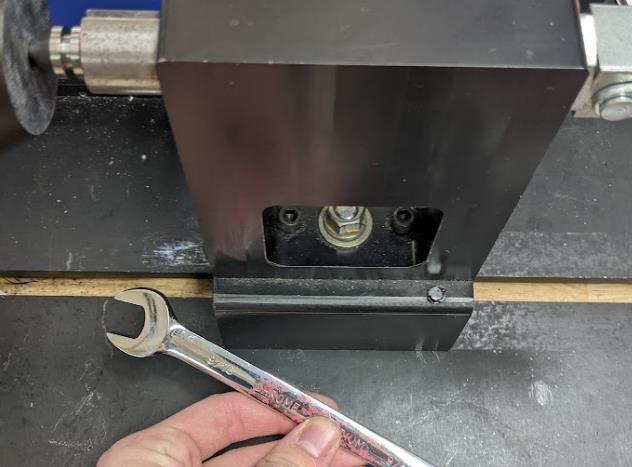
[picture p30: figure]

Figure 29. Move the chuck into the jig w/ 9/16” wrench.

Figure 30. Winding jig tightened in chuck with dead center moved into jig.

3.2.5 Feed the wire through the winder
With the wire fed through the guide loop immediately above the spool, the end of the wire should be clamped down in the chuck to prevent the wire from slipping during the initial windings, as shown in Figure 26 and 27. Note that the powered traverse (gray box on the right) and wire tensioner (the clear spools above the wire spool) are not used.

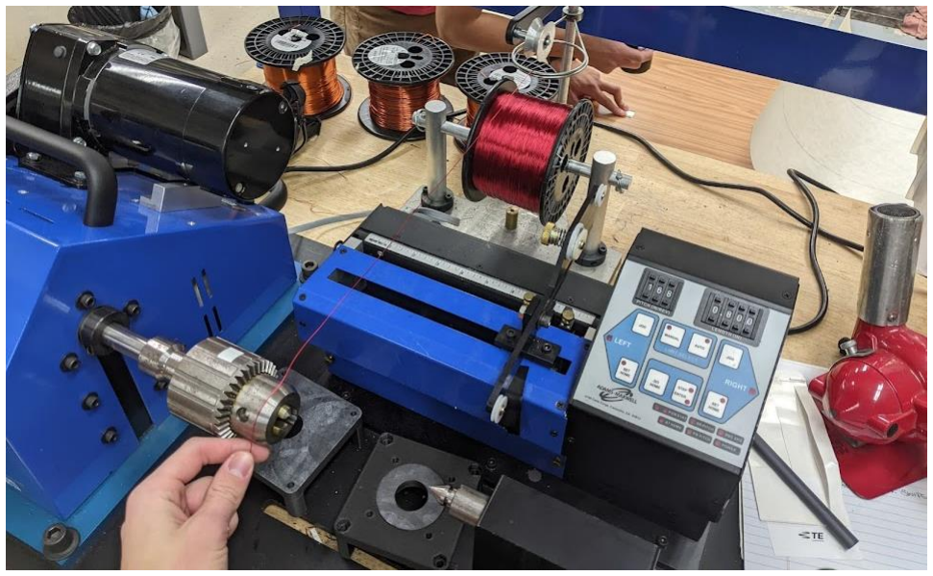
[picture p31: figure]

Figure 31. Guide loop threaded with 21-gauge wire from spool (ignore tensioners).

Figure 32. Wire pinched in chuck to prevent spinning.

3.2.6 Begin winding
Once everything is set and the machine is powered, step on the pedal to begin the winding process. Ensure all the windings sit nicely on the jig by guiding it with a finger. The image below shows ideal wrappings, but wrappings can cross and overlap without any drop in performance. Stop the winder when the counter reaches 135 turns. The number of turns is indicated on the panel above the switch and speed settings adjusted previously.

Figure 33. Initial wrappings.

3.2.7 Remove winding from winder
Once finished, grip the wire firmly on the winding jig and hold while cutting the wire. Carefully remove the jig from the chuck while ensuring that the windings do not come undone. Pull the coil from the chuck and use tape or extra wire to secure the coil. Repeat step 3.2.5 to 3.2.7 until you have 6 total coils. Once they are removed from the jig, squeeze them into an oval shape as seen in the image on the right below. This will help with inserting the windings into the stator slots.

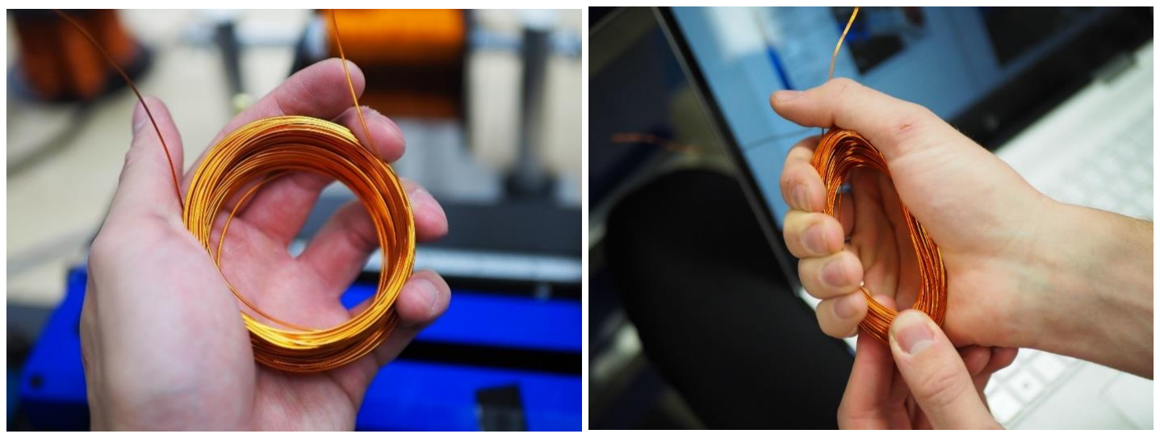
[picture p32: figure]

Figure 34. Windings taken off jig.
3.2.8 Insert windings
The next step is inserting the windings into the stator slots. A winding diagram is shown in Figure 35 below. It is crucial that the coils are inserted in the defined orientation. The following steps will outline this process.

Figure 35. Winding Diagram.

Label the slots and the sides on the stator with a marker as shown in Figure 36 and 37 below.

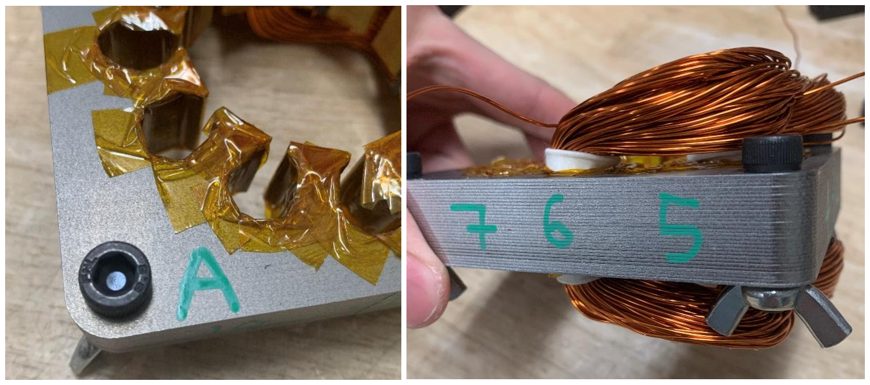
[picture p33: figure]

Figure 36 and 37. Labeling side and slot numbers on stator lamination.

Take a coil and insert it into one of stator gaps as seen in the Figure 38 below. Slowly and carefully insert the windings into the slots. Ensure all wire ends are sticking out on Side A.

Figure 38. Inserting windings into stator slot.

Once a side is fully inserted, slide the 3D printed retainer above the winding the stator slot to keep windings in place. The retaining tabs were implemented for manufacturability, helping to keep one side of the coil in its respective slot as the other side is pulled to the pairing slot.

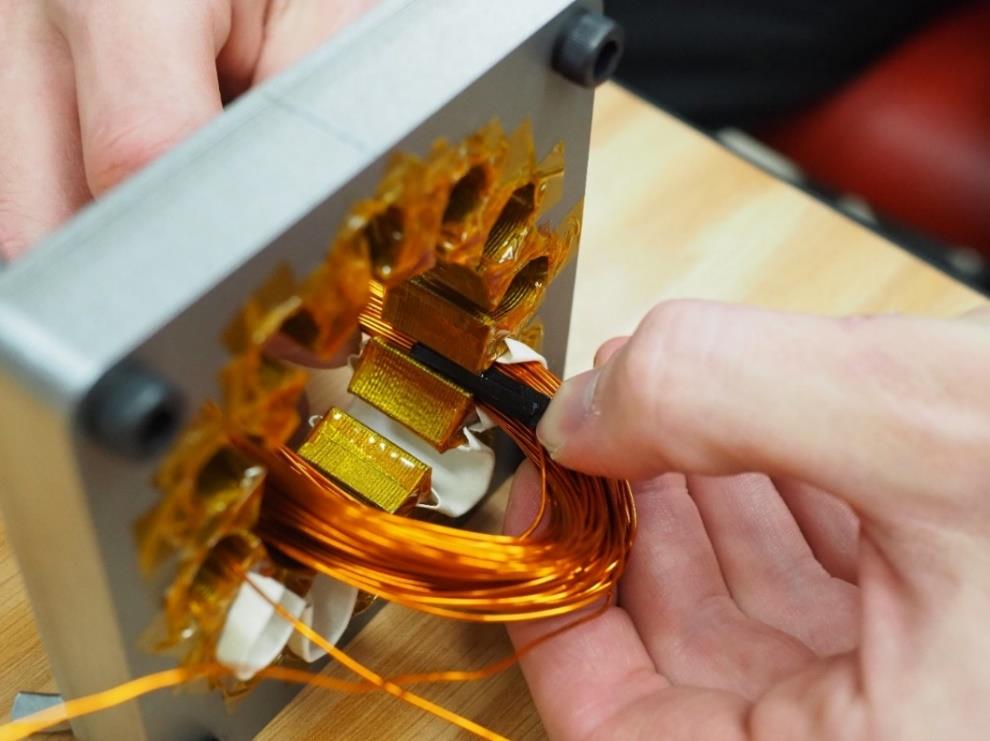
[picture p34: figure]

Figure 39. Inserting winding retainer into stator slot.

Repeat this inserting step with the other side of the winding three slots down in either direction from the first. Once this is completed, a screwdriver may be used to help bend the winding out of the way of other slots as seen below. Be careful and not to damage the varnish on the copper wires by scraping them while inserting the screwdriver.

Figure 40. Use a screwdriver to assist bending the coil.

Bend the winding by hand and/or gently tapping with a mallet to reduce the endwindings protruding from the slots.

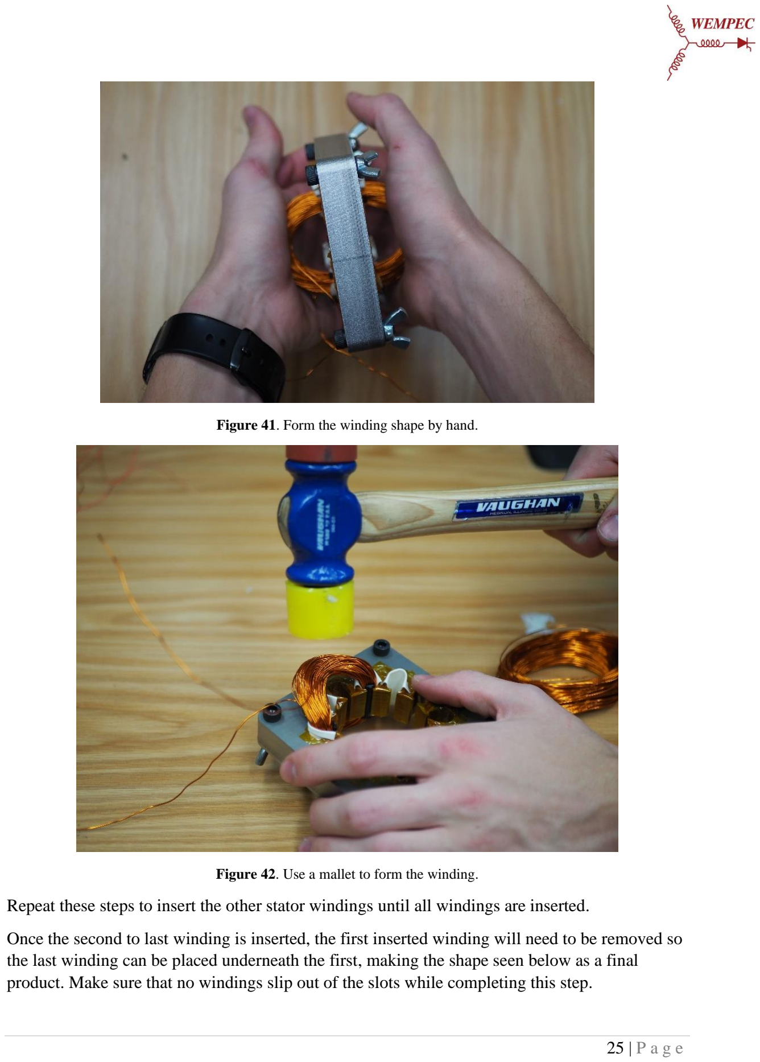
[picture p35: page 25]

Figure 41. Form the winding shape by hand.

Figure 42. Use a mallet to form the winding.

Repeat these steps to insert the other stator windings until all windings are inserted.

Once the second to last winding is inserted, the first inserted winding will need to be removed so the last winding can be placed underneath the first, making the shape seen below as a final product. Make sure that no windings slip out of the slots while completing this step.

Figure 43. Inserting second winding.

Once the windings are all inserted into the stator, label them based off which slot the wires is coming out of and whether it is a positive or negative terminal as determined by the diagram in Figure 35. Labelling the windings is extremely useful in troubleshooting and to become more familiar with the design in general.

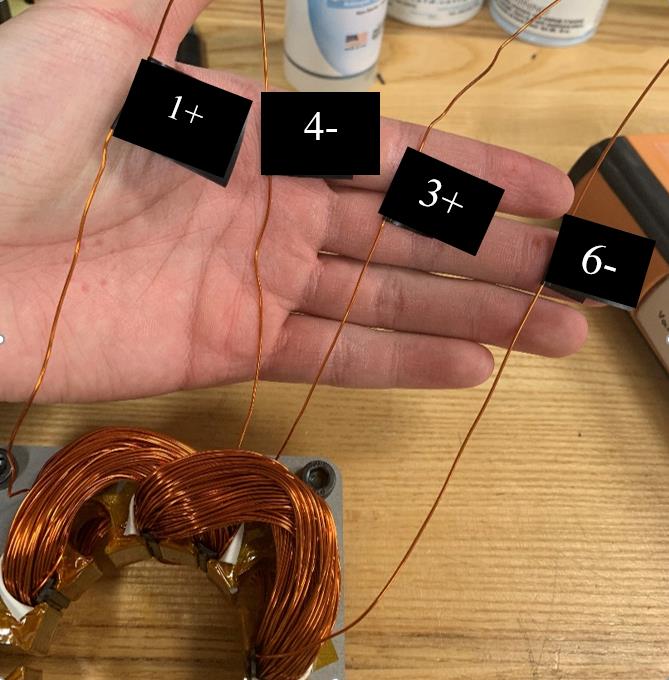
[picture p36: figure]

Figure 44. Label each coil terminal with tape.

Figure 45. Stator with all windings inserted.

Figure 46. Stator side view.

3.2.9 Apply heat-shrink tubing
Apply heat shrink tubing to each end of the coils to provide protection as shown below in Figure
47. You do not need to apply heat as long as the tubing is relatively snug on the wire.

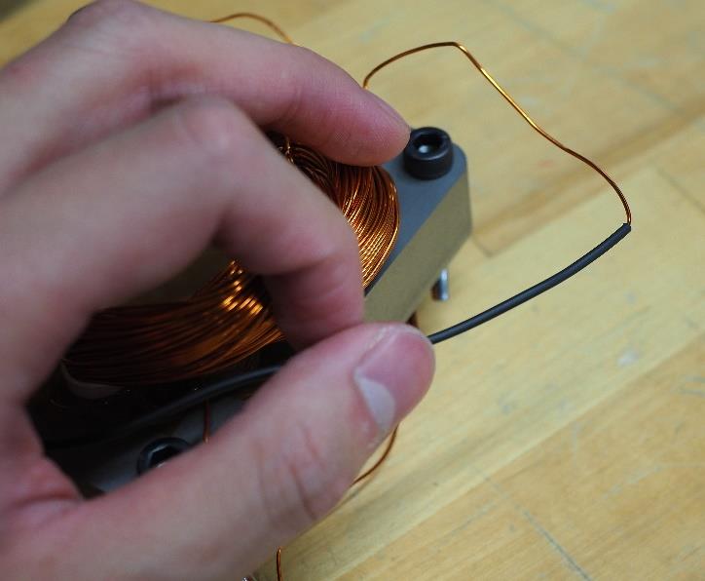
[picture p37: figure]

Figure 47. Inserting heat shrink tube to coils.

3.2.10 Perform High-Pot Test on stator windings
To ensure the winding are intact and not shorted to the stator or to other coil, a high-pot test should be performed. When performing the high-pot test, please ensure that your body does not have any direct contact with the positive lead.

Figure 48. A high-pot test machine.

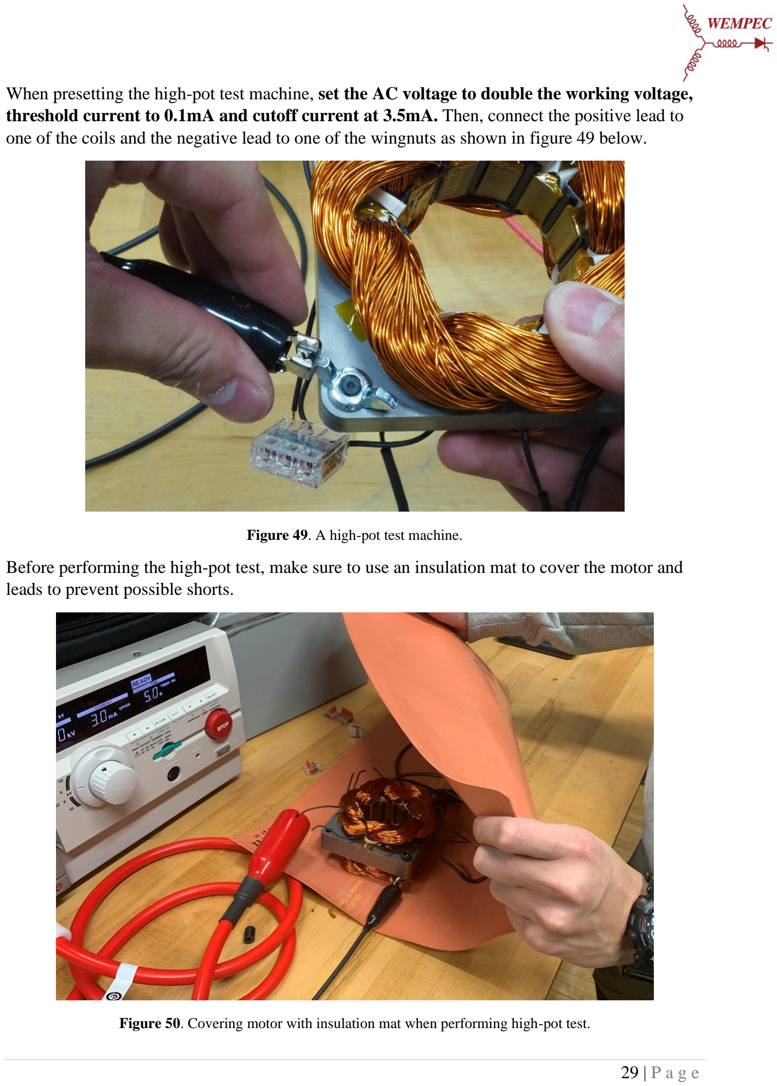
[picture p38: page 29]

When presetting the high-pot test machine, set the AC voltage to double the working voltage, threshold current to 0.1mA and cutoff current at 3.5mA. Then, connect the positive lead to one of the coils and the negative lead to one of the wingnuts as shown in figure 49 below.

Figure 49. A high-pot test machine.

Before performing the high-pot test, make sure to use an insulation mat to cover the motor and leads to prevent possible shorts.

Figure 50. Covering motor with insulation mat when performing high-pot test.

If the test fails, a buzzer will go off and the “FAIL” indicator will show up on the high-pot machine’s digital display.

Figure 51. High-Pot machine when test failed.

A failed test indicates that the coil is shorted to the stator lamination. To resolve this, you can either insert more insulation paper or swap out the problematic coil with a new one. Repeat this test for all coils in the stator.

3.2.11 Connecting coils
Once the hot-pot test has passed for all the winding coils, use clamp down wire connectors to connect all coils according to Figure 35 where wire 4 connects to 7, 6 connects to 9, and 8 connects to 11. Note, this motor is connected in a STAR configuration, terminals coming out from slots 10, 12 and 2 are all connected with a three-way clamp down wire connector to cancel out the current input of all windings.

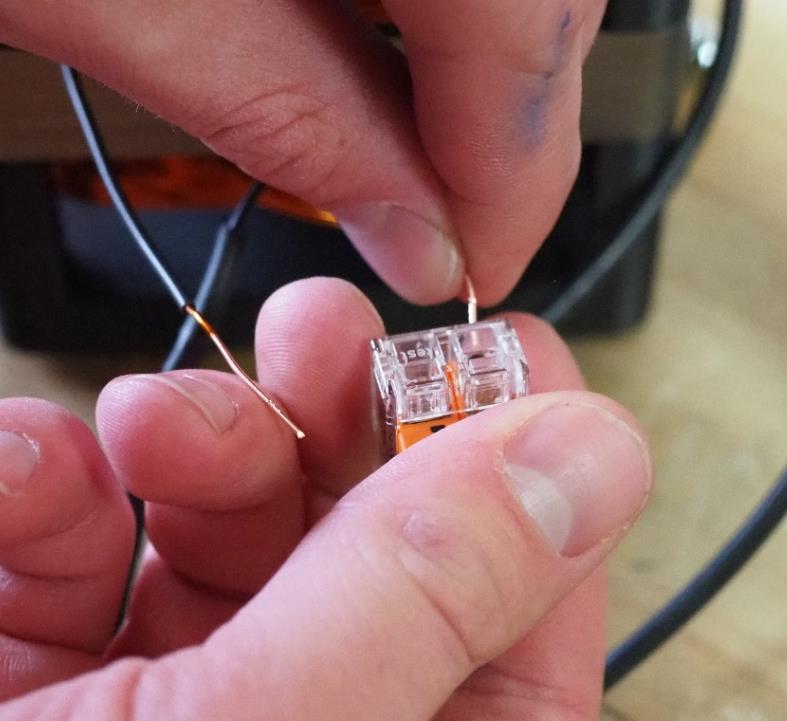
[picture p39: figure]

Figure 52. Connecting coils using clamp down wire connectors.

3.2.12 Soldering U, V and W terminals to banana plugs.
Solder the remaining U, V and W terminals (1, 3, & 5) to banana plugs to finish the stator assembly shown in Figure 53.

Figure 53. Final stator assembly with banana plugs connected.

### 3.3 End Plates

Two carbon fiber impregnated nylon end plates are printed to house the stator, bearings, and rotor. The end plates ensure proper alignment between the stator and rotor. Together the end plates form a housing around the motor and provide structure for wire management. Additionally, the endplates also serve a purpose of mounting to a test stand for performance evaluation. This endplate design specifically uses the IEC 63 standard for the mounting feature.

Take precautions to not break the extruded mounting holes off the end plates.

Parts and Materials

Table 4. Parts needed for end plate assembly.

Part | Quantity
3D Printed End Plate (Circular Mounting Holes) | 1
3D Printed End Plate (Hex Mounting Holes) | 1
25mm ID No. 6201 Ball Bearing | 2
M4 Threaded Inserts | 4

3.3.1 Insert the bearings
Insert a bearing on each endplate. The hole should be snug enough to hold the bearings in place after insertion. If needed, use a rubber mallet to tab the bearing into place. Ensure that the bearing is parallel to the end plate face. The end plate without the emboss feature will be the top of the motor and requires no further assembly.

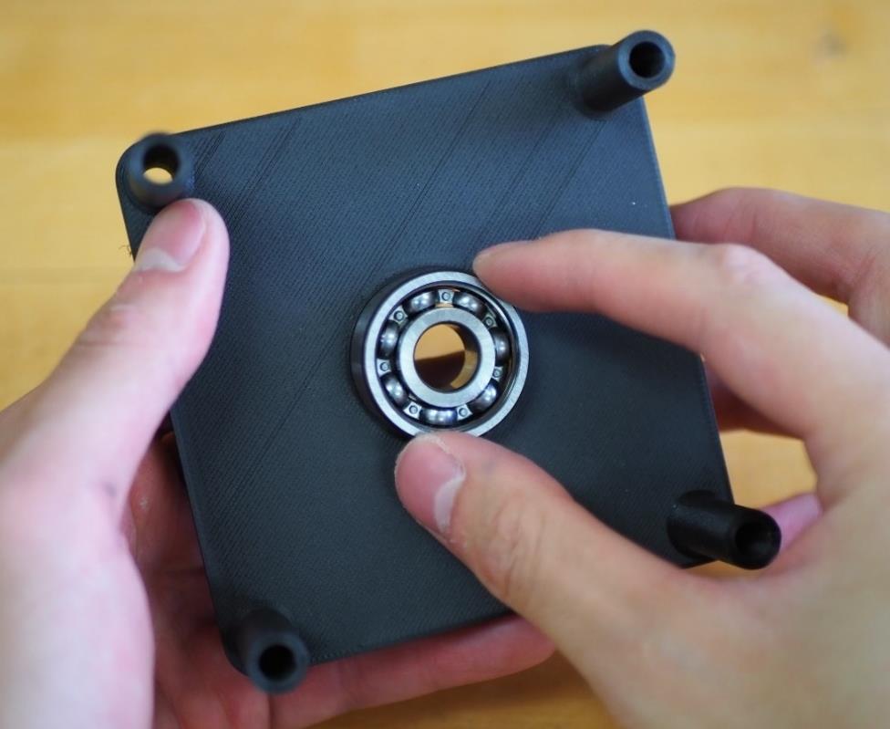
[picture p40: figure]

Figure 54. Inserting the bearings.

3.3.2 Insert the threaded inserts
Using a heated soldering iron, press down on the threaded inserts, placed near the center boss as shown below in Figure 55. The end plate material will melt away, allowing the threaded insert to be put in place. Ensure that the inserts are placed straight. Take precautions to not melt other parts of the endplate when using the soldering iron. Repeat this step for all the through holes. This end plate will be the bottom of the motor housing.

Figure 55. Thermosetting the threaded insert with a heated soldering iron.

### 3.4 Final Assembly

The final assembly process is quick and simple. All components should now be ready to be placed into the final assembly. These include the end plates, stator, rotor, and M6 bolts with locking nuts, as shown in Figure 56.

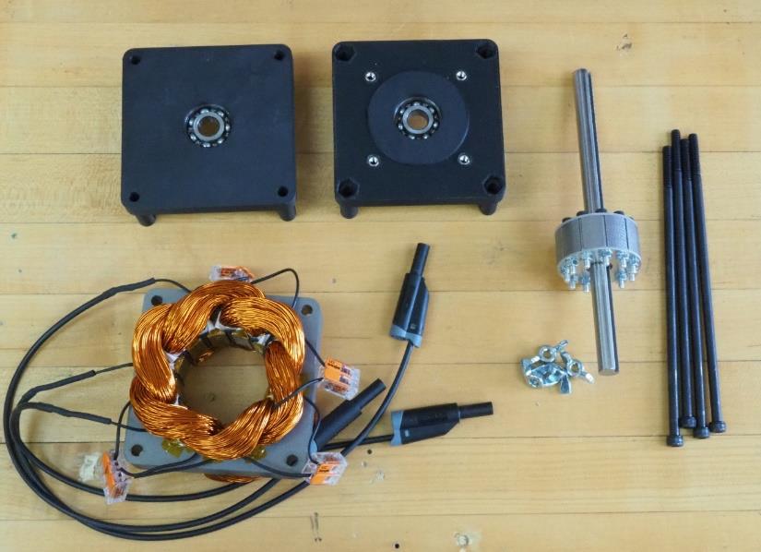
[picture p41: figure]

Figure 56. Parts prepared for final assembly.

Parts and Materials

Table 5. Parts needed for final assembly.

Part | Quantity
End Plate with Bearing | 1
End Plate with Bearing and Threaded Insert | 1
Completed Stator Assembly | 1
Completed Rotor Assembly | 1
M6 130mm Bolts | 4
M6 Locking Wing Nuts | 4

3.4.1 Placing the M6 bolts into position
Place the bolts into the end plate that has the four now threaded sections towards the middle as shown in Figure 57.

Figure 57. Placing the M6 bolts into the end plates.
3.4.2 Place the stator assembly into position
Place the four corners of the stator assembly through the bolts with the terminals facing up as shown in Figure 58.

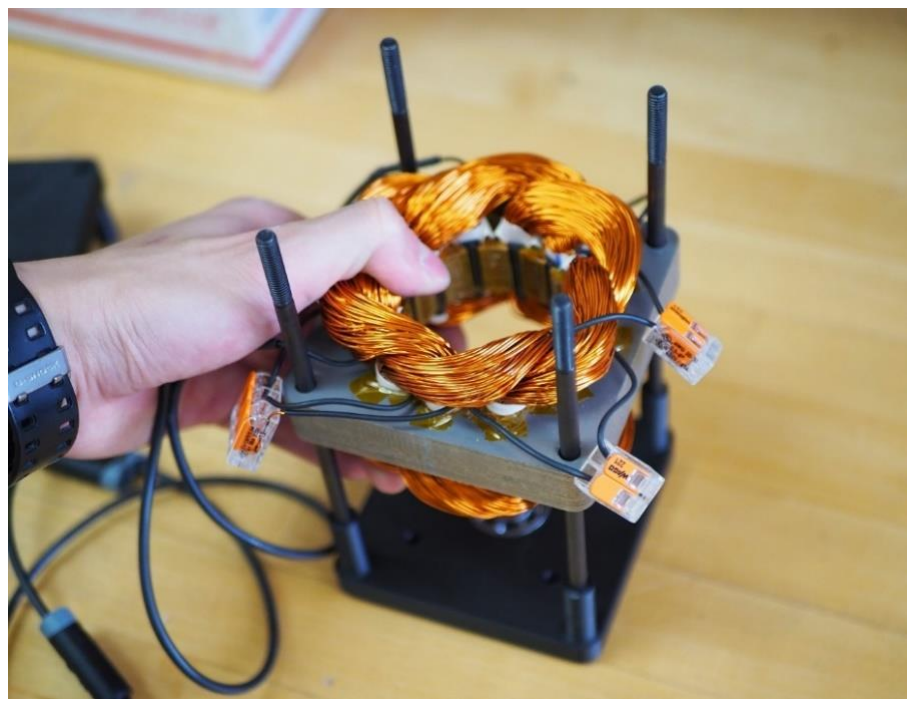
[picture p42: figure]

Figure 58. Adding the stator to the final assembly.

3.4.3 Place the stator assembly into position
Ensure that all the windings are out of the way so the rotor assembly can fit and spin without any interference. Place the rotor with the top of the bolts placing upward. Force will need to be applied; push until the rotor is flush with the stator as shown in Figure 59.

Figure 59. Adding the rotor to the final assembly.
3.4.4 Place the other end plate and complete the assembly
Place the second end plate through the bolts as shown in Figure 60. Use the nuts to keep the end plates in place. Finally, ensure the stator and rotor assemblies are placed at the center in between the two end plates.

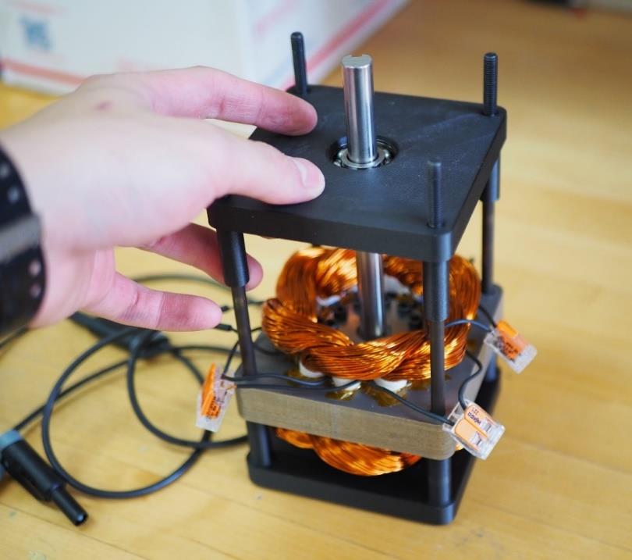
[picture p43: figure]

Figure 60. Adding the second end plate to the final assembly.

Figure 61. Fully assembled induction motor.

## 4 Appendix

### 4.1 Drawings

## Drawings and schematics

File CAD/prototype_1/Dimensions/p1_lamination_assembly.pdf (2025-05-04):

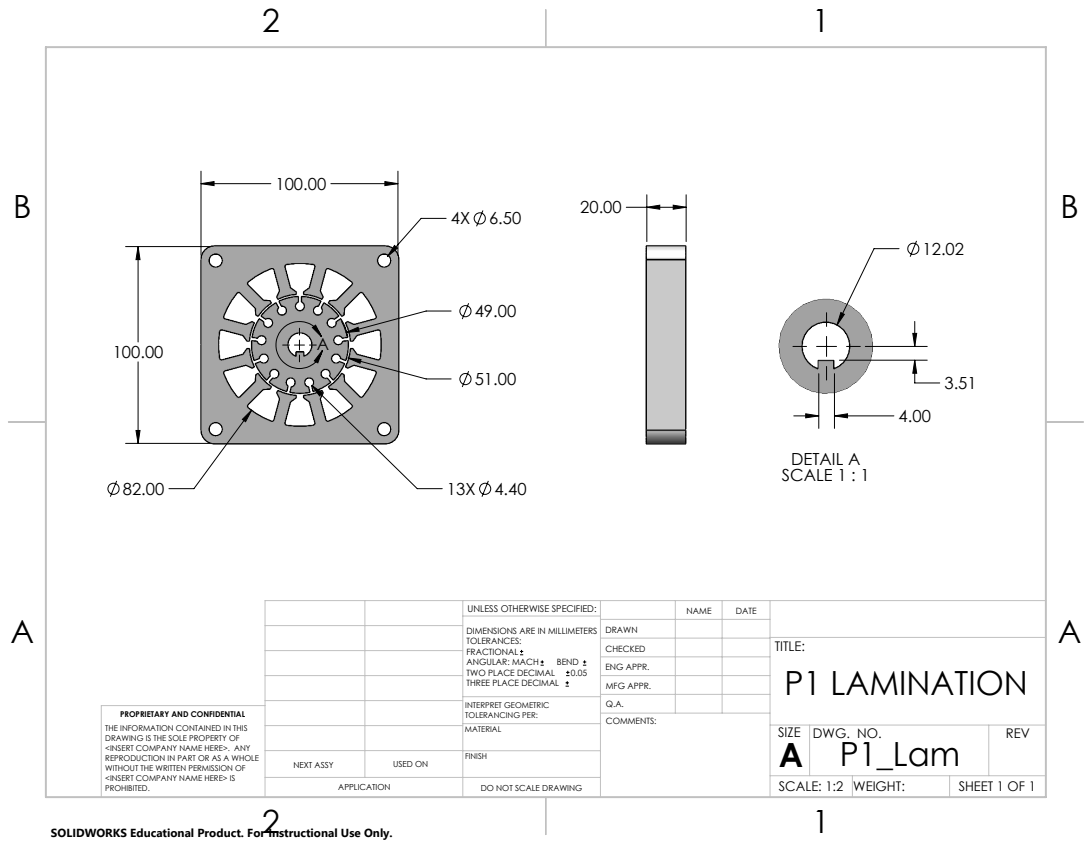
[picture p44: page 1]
DETAIL A SCALE 1 : 1

UNLESS OTHERWISE SPECIFIED: | | NAME | DATE
DIMENSIONS ARE IN MILLIMETERS TOLERANCES: FRACTIONAL ANGULAR: MACH BEND TWO PLACE DECIMAL 0.05 THREE PLACE DECIMAL | DRAWN

CHECKED | | | TITLE: P1 LAMINATION

ENG APPR.
MFG APPR.

INTERPRET GEOMETRIC TOLERANCING PER: | Q.A.
MATERIAL | | SIZE A | DWG. NO. P1_Lam | REV

PROPRIETARY AND CONFIDENTIAL
THE INFORMATION CONTAINED IN THIS
DRAWING IS THE SOLE PROPERTY OF
<INSERT COMPANY NAME HERE>. ANY
REPRODUCTION IN PART OR AS A WHOLE
WITHOUT THE WRITTEN PERMISSION OF
<INSERT COMPANY NAME HERE> IS
PROHIBITED.

NEXT ASSY | USED ON | FINISH

APPLICATION | DO NOT SCALE DRAWING | | SCALE: 1:2 | WEIGHT: | SHEET 1 OF 1

SOLIDWORKS Educational Product. For Instructional Use Only.

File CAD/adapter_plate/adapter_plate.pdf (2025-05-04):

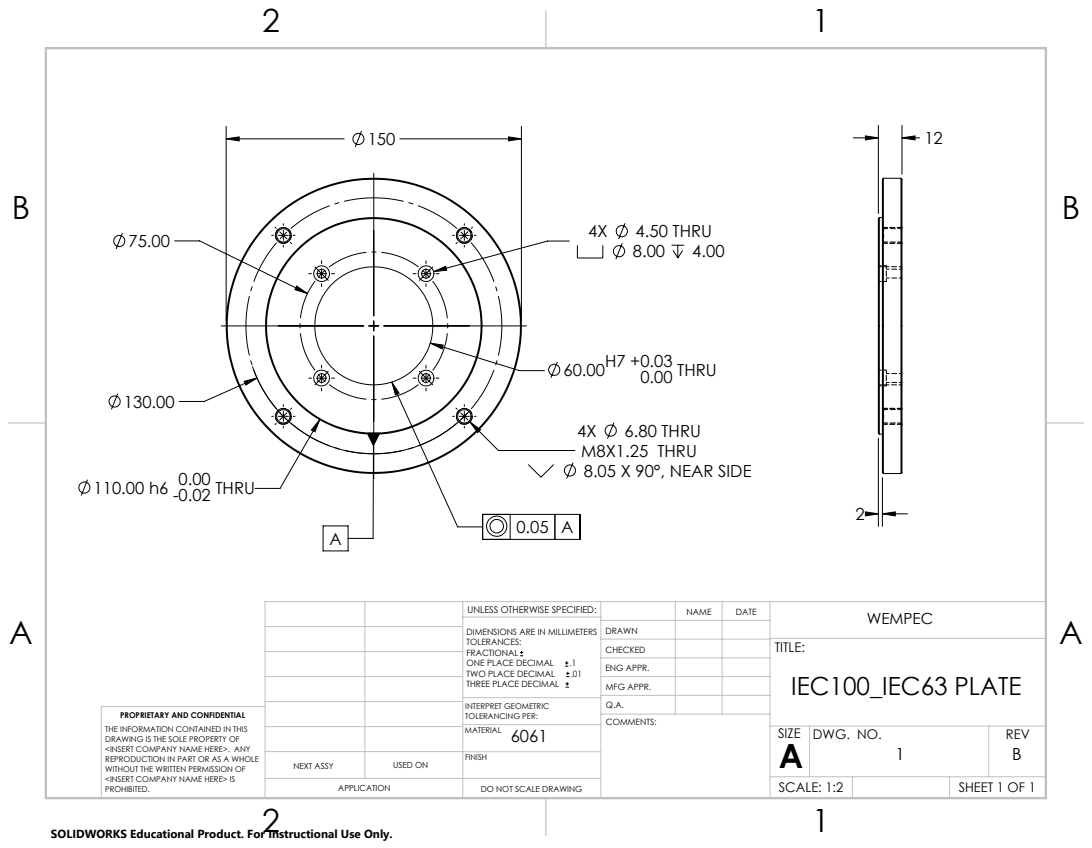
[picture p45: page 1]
6.80 THRU; M8X1.25 THRU 8.05 X 90°, NEAR SIDE; 4.50 THRU; 0.02 THRU; 60.00H7 +0.03 0.00 THRU

UNLESS OTHERWISE SPECIFIED: | | NAME | DATE | WEMPEC
DIMENSIONS ARE IN MILLIMETERS TOLERANCES: FRACTIONAL ONE PLACE DECIMAL .1 TWO PLACE DECIMAL .01 THREE PLACE DECIMAL | DRAWN

CHECKED | | | TITLE: IEC100_IEC63 PLATE

ENG APPR.
MFG APPR.

INTERPRET GEOMETRIC TOLERANCING PER: | Q.A.

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

USED ON | MATERIAL 6061 | | SIZE A | DWG. NO. 1 | REV B

NEXT ASSY | | FINISH

APPLICATION | DO NOT SCALE DRAWING | | SCALE: 1:2 | | SHEET 1 OF 1

SOLIDWORKS Educational Product. For Instructional Use Only.

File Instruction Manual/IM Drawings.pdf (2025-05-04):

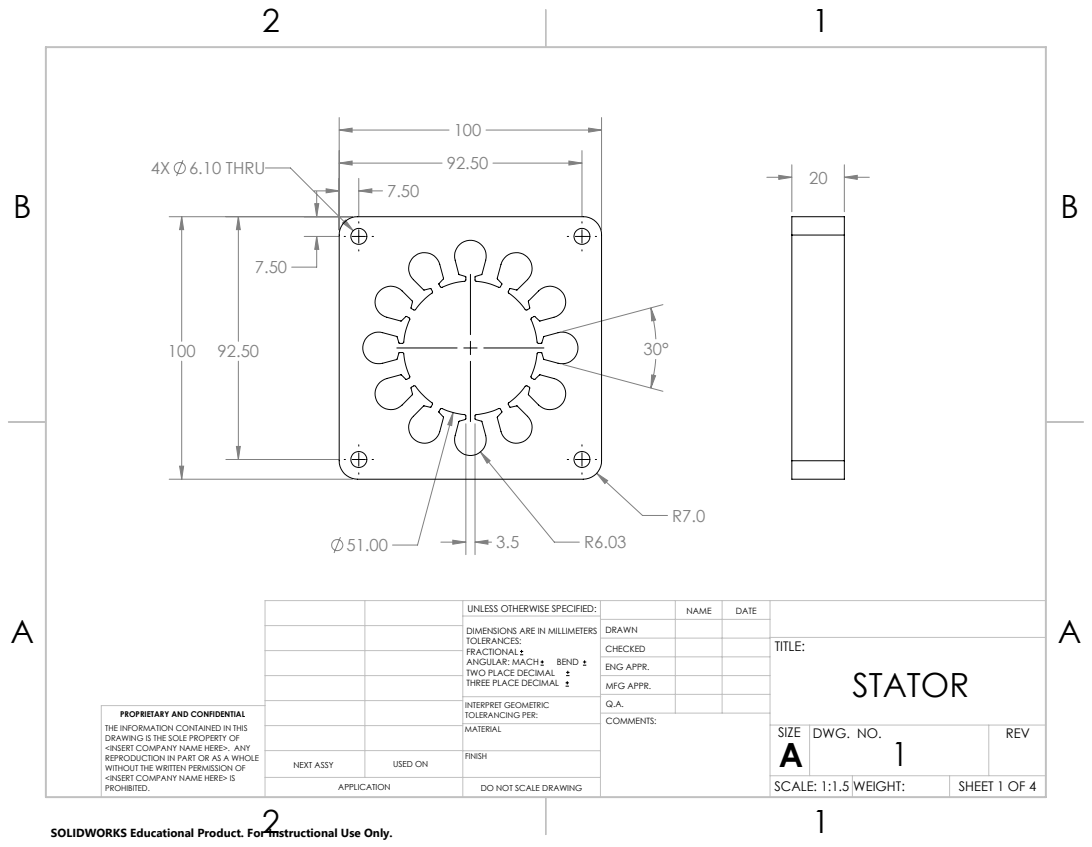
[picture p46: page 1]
4X 6.10 THRU

UNLESS OTHERWISE SPECIFIED: | | NAME | DATE
DIMENSIONS ARE IN MILLIMETERS TOLERANCES: FRACTIONAL ANGULAR: MACH BEND TWO PLACE DECIMAL THREE PLACE DECIMAL | DRAWN

CHECKED | | | TITLE: STATOR

ENG APPR.
MFG APPR.

INTERPRET GEOMETRIC TOLERANCING PER: | Q.A.
MATERIAL | | SIZE A | DWG. NO. 1 | REV

PROPRIETARY AND CONFIDENTIAL
THE INFORMATION CONTAINED IN THIS
DRAWING IS THE SOLE PROPERTY OF
<INSERT COMPANY NAME HERE>. ANY
REPRODUCTION IN PART OR AS A WHOLE
WITHOUT THE WRITTEN PERMISSION OF
<INSERT COMPANY NAME HERE> IS
PROHIBITED.

NEXT ASSY | USED ON | FINISH

APPLICATION | DO NOT SCALE DRAWING | | SCALE: 1:1.5 WEIGHT: | | SHEET 1 OF 4

SOLIDWORKS Educational Product. For Instructional Use Only.

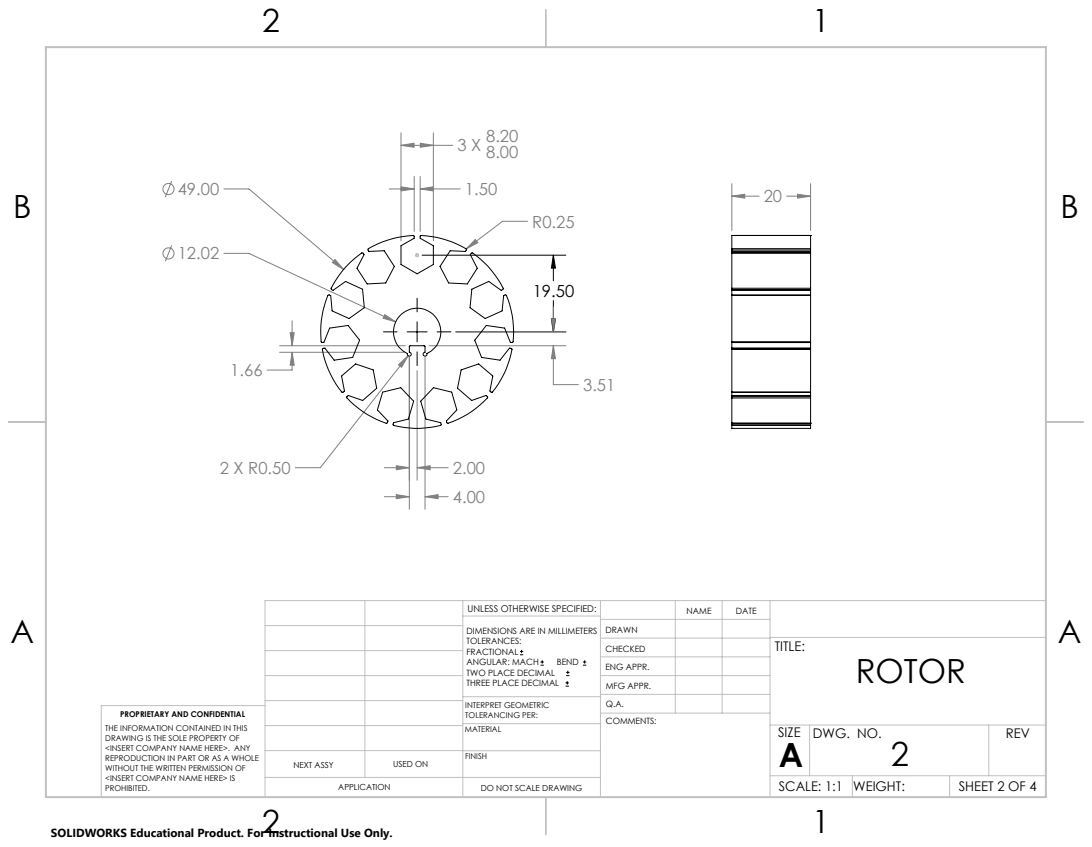
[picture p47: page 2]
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

CHECKED | | | TITLE: ROTOR

ENG APPR.
MFG APPR.

INTERPRET GEOMETRIC TOLERANCING PER: | Q.A.
MATERIAL | | SIZE A | DWG. NO. 2 | REV

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

NEXT ASSY | USED ON | FINISH

SCALE: 1:1 | WEIGHT:

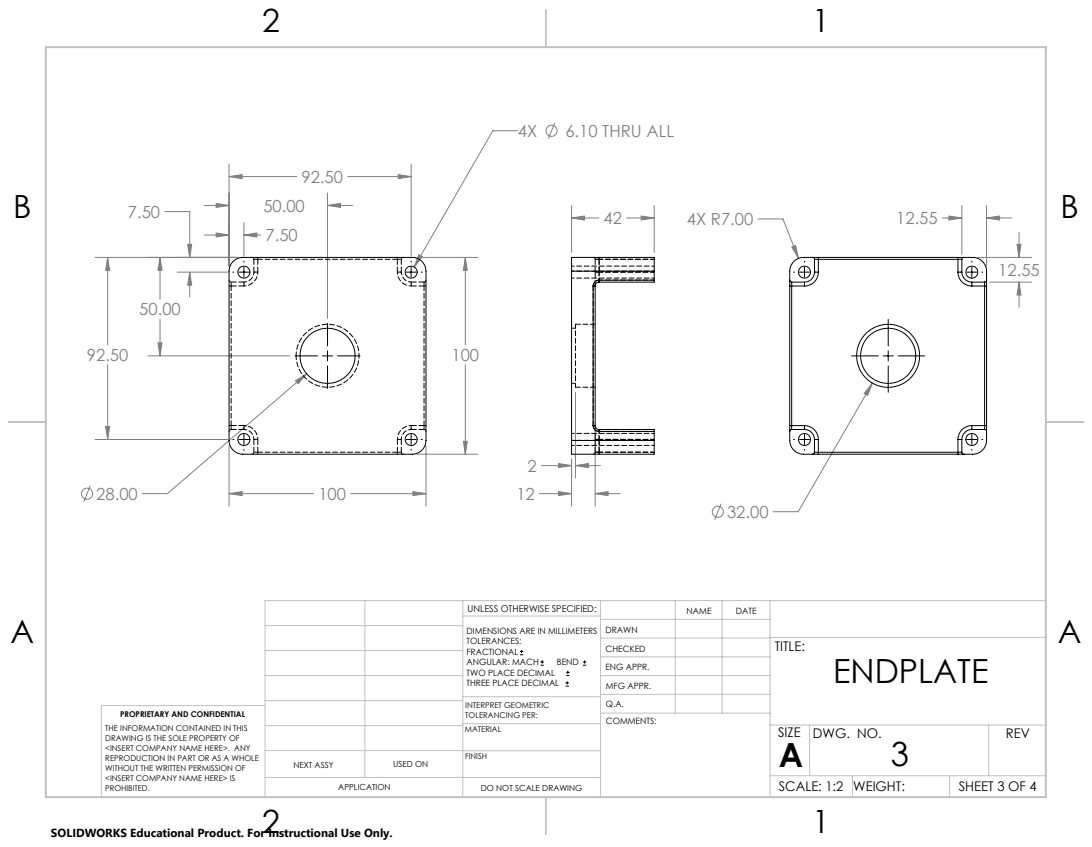
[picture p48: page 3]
6.10 THRU ALL

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

CHECKED | | | TITLE: ENDPLATE

ENG APPR.
MFG APPR.

INTERPRET GEOMETRIC TOLERANCING PER: | Q.A.
MATERIAL | | SIZE A | DWG. NO. 3 | REV

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

NEXT ASSY | USED ON | FINISH

SCALE: 1:2 | WEIGHT:

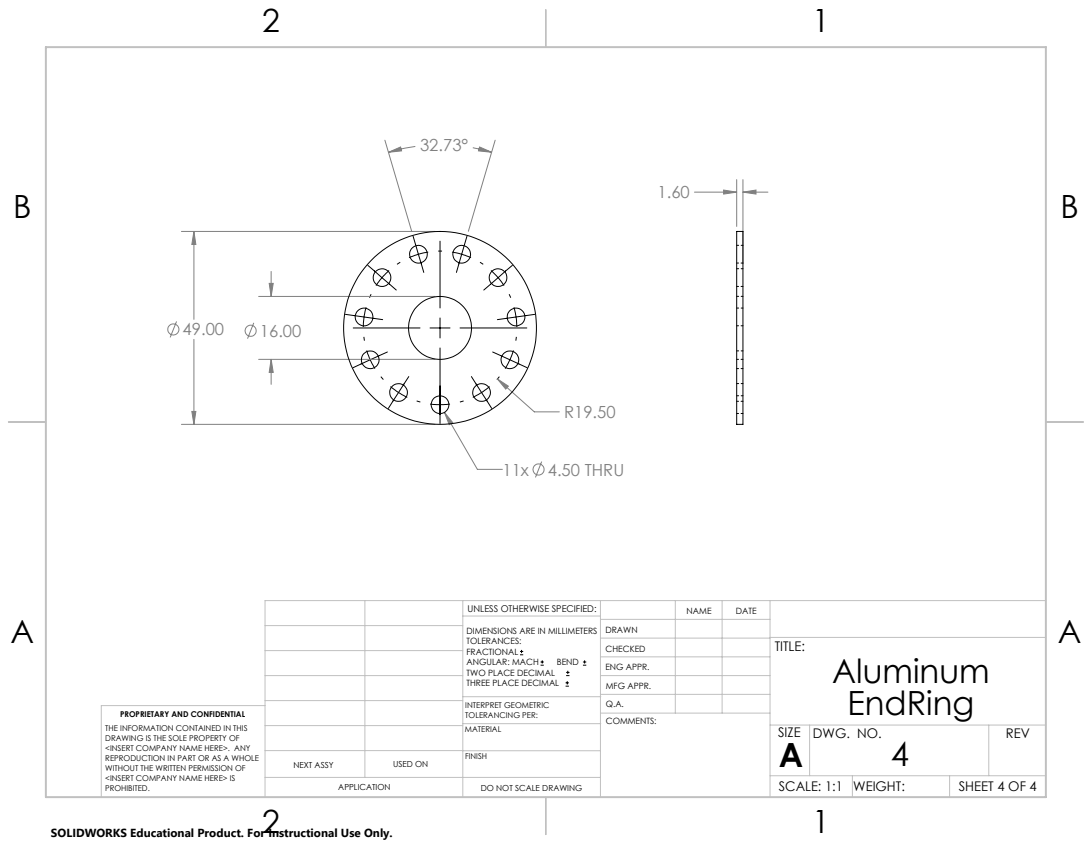
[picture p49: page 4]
11x 4.50 THRU

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

CHECKED | | | TITLE: Aluminum EndRing

ENG APPR.
MFG APPR.

INTERPRET GEOMETRIC TOLERANCING PER: | Q.A.
MATERIAL | | SIZE A | DWG. NO. 4 | REV

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

NEXT ASSY | USED ON | FINISH

SCALE: 1:1 | WEIGHT:

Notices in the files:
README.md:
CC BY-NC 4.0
